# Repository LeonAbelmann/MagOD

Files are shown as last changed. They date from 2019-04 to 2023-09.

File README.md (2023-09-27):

# MagOD
Magnetic Optical Density meter
Tijmen Hageman, Jordi Hendrix, Hans Keizer, Marcel Welleweerd, Dave
van As, Ruthvik Bandaru, Rob Krawinkel, Leon Abelmann.

KIST Europe, University of Twente

## Other sources
Next to software, also the source codes to create hardware are
available here, as well as :

- Measurement head design, 3D print file (OpenSCAD, on [Thingiverse](https://www.thingiverse.com/thing:3122930) )
- Spice simulations, electronic diagrams, PCB layout (Spice, KiCad on
  [Dropbox](https://www.dropbox.com/sh/1dcai82byvd3hy0/AAA3AGXw0jbr9n2gzdcszufia))
- Laser cut pattern for housing electronics (DXF, on [Dropbox](https://www.dropbox.com/sh/1dcai82byvd3hy0/AAA3AGXw0jbr9n2gzdcszufia))

## Specifications
- Up to 800 samples per second, allows precise analysis of the rotation speed of magnetic bacteria
- Three-dimensional quasi-Helmholtz configuration, with fields up to 5 mT 
- Three color LED: red: 645 nm, 1000 mcd, green: 520 nm, 1700 mcd and blue 460 nm, 500 mcd
- Power supply with current feedback to compensate for coil heating, cut-off frequency 200 Hz
- Large area photodiode (sensitivity 0.5 mlx, with green LED theoretical max OD range of 5.8)
- Integrated pre-amplifier, SNR 83 dB (max OD range 4.0).
- Dedicated 16-bit ADS1115 DA converter
- Integrated temperature sensor
- Reference light detector
- Scattered light detector
- Fully programmable (ESP32 using Arduino IDE), open source
- User friendly spreadsheet recipe definition (csv format), with software to validate correctness
- Data collection on SD card, accessible by ftp over Wifi

## Additional info
- Marcel Welleweerd *and colleagues* (2022) ["An open-source automated magnetic optical density meter for analysis of suspensions of magnetic cells and particles"](https://doi.org/10.1063/5.0098008) Review of Scientific Instruments Vol 93, Issue 9, 094101. The manuscript can be found on [ArXiv](https://arxiv.org/abs/2106.07466)
- Chapter 8 in [Thesis](https://research.utwente.nl/en/publications/observing-magnetic-objects-in-fluids) Tijmen Hageman.
- [Presentation](https://youtu.be/TwwIsPg0qnI) by Leon Abelmann at Intermag2021

## How to join
Send mail to Leon (l.abelmann@tudelft.nl) if you are interested, all skills are welcome.

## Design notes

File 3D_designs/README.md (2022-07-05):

# Design 3D print housing
OpenScad design files and stl outputs

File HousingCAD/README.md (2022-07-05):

# CAD Design housing
Files for laser cutting housing

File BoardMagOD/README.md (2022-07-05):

# Measurement Board
Electronic design of measurement board

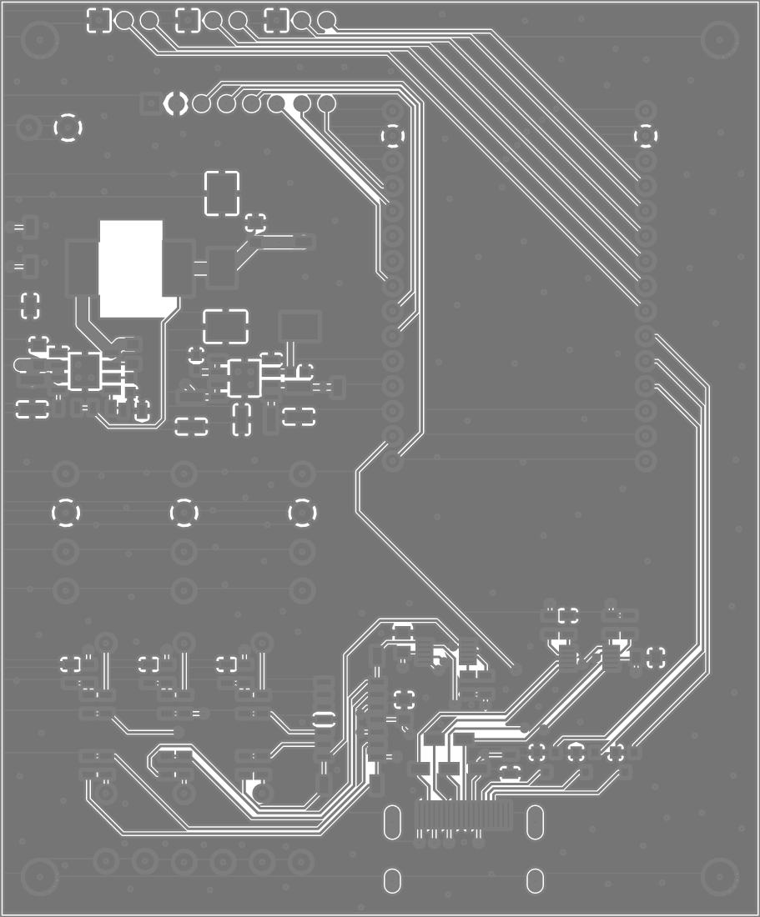
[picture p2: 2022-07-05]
BoardMagOD/mask.png

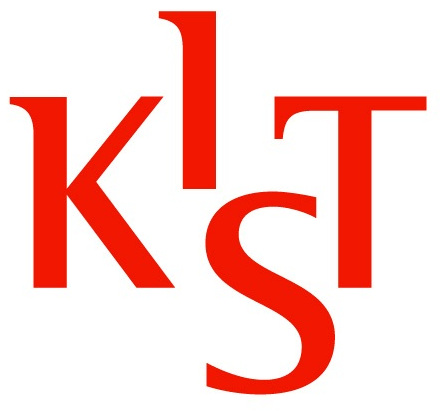
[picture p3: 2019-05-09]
matlab/MagOD_Cmag/magod.jpg

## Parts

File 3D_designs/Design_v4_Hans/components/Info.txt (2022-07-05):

Diverse components of the OD setup of Hans, Jordi and Tijmen.

Needed amount of the components:
1x coil_open
1x cuvette
1x frame
1x ledholder
1x toplid
4x coils

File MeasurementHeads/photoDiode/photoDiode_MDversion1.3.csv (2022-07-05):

Reference | Quantity | Value | Footprint | Datasheet | Article number
C1 | 1 | 0.1uF | Capacitors_SMD:C_0805 | https://nl.farnell.com/wurth-elektronik/885012207016/cap-0-1-f-10v-10-x7r-0805/dp/2534051 | 8.85012E+11
C2 C5 | 2 | C | Capacitors_SMD:C_0805 | ~
C3 | 1 | 1.5uF | Capacitors_SMD:C_0805 | https://nl.farnell.com/multicomp/mc0805x155k6r3ct/cap-1-5-f-6-3v-10-x5r-0805/dp/1759410 | MC0805X155K6R3CT
C4 | 1 | 47uF | Capacitors_SMD:C_0805 | https://nl.farnell.com/murata/grm21br60j476me15l/cap-47-f-6-3v-20-x5r-0805/dp/2362109 | GRM21BR60J476ME15L
D1 | 1 | BPW21 | Package_TO_SOT_THT:TO-5-2_Window | http://techwww.in.tu-clausthal.de/site/Dokumentation/Dioden/Fotodioden/BPW21-Fotodiode.pdf | BPW21R
D2 | 1 | D | Diodes_SMD:D_SOD-123 | ~
J1 | 1 | Conn_01x03 | Connector_Molex:Molex_Pico-Clasp_501331-0307_1x03-1MP_P1.00mm_Vertical | https://nl.farnell.com/molex/501331-0307/connector-header-3pos-1row-1mm/dp/1835977?st=pico%20clasp | 501331-0307
L1 | 1 | Ferrite_Bead | Inductor_SMD:L_0805_2012Metric | https://nl.farnell.com/murata/blm21bd272sn1l/ferrite-bead-0-8ohm-200ma-0805/dp/1515647 | BLM21BD272SN1L
MH1 MH2 | 2 | MountingHole | Mounting_Holes:MountingHole_2.2mm_M2 | ~
R1 R3 R4 R6 | 4 | R | Resistor_SMD:R_0805_2012Metric | ~
R2 | 1 | 3 | Resistor_SMD:R_0805_2012Metric | https://nl.farnell.com/panasonic-electronic-components/erj6geyj3r0v/res-3r-5-0-125w-0805-thick-film/dp/2323844RL | ERJ6GEYJ3R0V
U1 | 1 | Opamp_Dual_Generic | Housings_SOIC:SOIC-8_3.9x4.9mm_Pitch1.27mm | https://nl.mouser.com/ProductDetail/Texas-Instruments/OPA2140AID | OPA2140AID
U2 | 1 | EMIshield | EMIshield:Laird-BMI-S-202-F | https://nl.farnell.com/laird/bmi-s-202-f/emi-shield-surface-mount/dp/2497717?ost=BMI-S-202-F&scope=partnumberlookahead&searchref=searchlookahead | BMI-S-202-F

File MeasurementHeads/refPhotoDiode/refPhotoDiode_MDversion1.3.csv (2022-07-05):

Id | Designator | Package | Quantity | Designation | Supplier and ref
1 | R1,R2 | R_0805_2012Metric | 2 | R
2 | C1,C4 | C_0805 | 2 | C
3 | C2 | C_0805 | 1 | 1.5uF
4 | C3 | C_0805 | 1 | 0.1uF
5 | L1 | L_0805_2012Metric | 1 | Ferrite_Bead
6 | J1,J2 | PinHeader_1x04_P2.54mm_Vertical_SMD_Pin1Left | 2 | Conn_01x04
7 | U2 | Wurth-3610213126S-EMIshield-13.26x12.3mm | 1 | EMIshield
8 | REF** | MountingHole_2.2mm_M2 | 1 | MountingHole_2.2mm_M2
9 | J3 | Molex_Pico-Clasp_501331-0607_1x06-1MP_P1.00mm_Vertical | 1 | Conn_01x06
10 | D2 | D_SOD-123 | 1 | D
11 | D1 | TO-5-2_Window | 1 | BPW21
12 | U1 | SOT-23-5 | 1 | OPA140

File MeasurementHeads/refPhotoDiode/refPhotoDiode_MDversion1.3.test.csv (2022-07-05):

Reference |  | Value |  | Footprint | Datasheet | Article | number
D1 | BPW21 | BPW21:TO-5-2_Window | http://techwww.in.tu-clausthal.de/site/Dokumentation/Dioden/Fotodioden/BPW21-Fotodiode.pdf
C1 | 180p | Capacitors_SMD:C_0805 | ~
R1 | 1000k | Resistor_SMD:R_0805_2012Metric | ~
J1 | Conn_01x04 | Connector_PinHeader_2.54mm:PinHeader_1x04_P2.54mm_Vertical_SMD_Pin1Left | https://nl.farnell.com/samtec/tsm-104-04-t-sv/header-2-54mm-smt-4way/dp/2043897 | TSM-104-04-T-SV
J2 | Conn_01x04 | Connector_PinHeader_2.54mm:PinHeader_1x04_P2.54mm_Vertical_SMD_Pin1Left | https://nl.farnell.com/samtec/tsm-104-04-t-sv/header-2-54mm-smt-4way/dp/2043897 | TSM-104-04-T-SV
J3 | Conn_01x06 | Connector_Molex:Molex_Pico-Clasp_501331-0607_1x06-1MP_P1.00mm_Vertical | https://nl.farnell.com/molex/501568-0607/header-1-00mm-6way/dp/2060673?st=molex%20pico | 501331-0607
C2 | 1.5uF | Capacitors_SMD:C_0805 | https://nl.farnell.com/multicomp/mc0805x155k6r3ct/cap-1-5-f-6-3v-10-x5r-0805/dp/1759410 | MC0805X155K6R3CT
U2 | EMIshield | EMIshield:Wurth-3610213126S-EMIshield-13.26x12.3mm | https://nl.farnell.com/wurth-elektronik/3610213126s/emi-shield-cabinet-13-26mm-x-12/dp/2918354?ost=3610213126S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 | 3610213126S
L1 | Ferrite_Bead | Inductor_SMD:L_0805_2012Metric | https://nl.farnell.com/murata/blm21bd272sn1l/ferrite-bead-0-8ohm-200ma-0805/dp/1515647 | BLM21BD272SN1L
C3 | 0.1uF | Capacitors_SMD:C_0805 | https://nl.farnell.com/wurth-elektronik/885012207016/cap-0-1-f-10v-10-x7r-0805/dp/2534051 | 885012207016
R2 | 20k | Resistor_SMD:R_0805_2012Metric | ~
D2 | D | Diodes_SMD:D_SOD-123 | ~
C4 | 1u | Capacitors_SMD:C_0805 | ~
U1 | OPA140 | Package_TO_SOT_SMD:SOT-23-5 | http://www.ti.com/lit/ds/symlink/opa340.pdf

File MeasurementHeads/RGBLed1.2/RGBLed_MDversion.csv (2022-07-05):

Reference | Quantity | Value | Footprint | Datasheet
D1 | 1 | LED_RABG | KingbrightRGB:L-154A4SUREQBFZGEW | ~
J1 J2 | 2 | Conn_01x04 | Socket_Strips:Socket_Strip_Straight_1x04_Pitch2.54mm | ~
R1 R2 R3 | 3 | R | Resistors_SMD:R_0805 | ~

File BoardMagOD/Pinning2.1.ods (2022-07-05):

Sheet: SPI
ESP32 |  |  | ESP32 DEVKIT V1 J2 |  |  | MagBoard U3 |  |  | MagODBoard J3 |  |  | J3 flatcable | TFTM050Board |  |  | ES-AR-RA8875 | ES-AR-RA8875 | 74lv245 | Arduino |  | ES-AR-RA8875
 |  |  |  |  |  |  |  |  | 1 | 5V_b | red | brown | 3-4 | VDD | 1-8 JP1 | LCD-VDD | JP4-4 |  | Arduino 5V | JP4-4 | JP1-3/4
 |  |  |  |  |  |  |  |  | 2 | GND | black | red | 1-2 | VSS |  | VSS | JP4-3 |  | GND | Jp4-3 | JP1-1/2
37 | GPIO23 | low | VSPI_MOSI | 15 | GPIO23 | 30 | D23 | MOSI | 3 | MOSI_con | green | orange | 7 | SDI (MOSI) |  | CS-SDI-SDA | JP5-3 | U2 B2-A2 | MOSI | JP5-3 | JP1-7
31 | GPIO19/CTS0 | high | VSPI_MISO | 10 | GPIO19 | 25 | D19 | MISO | 4 | MISO_con | purple | yellow | 6 | SDO (MISO) |  | WR/SDO | JP5-6 | U1 A0-B0 | MISO | JP5-6 | JP1-6
30 | GPIO18 | low | VSPI_SCK | 9 | GPIO18 | 24 | D18 | SCK | 5 | SCK_con | white | green | 8 | SCLK |  | RS/SCLK | JP5-4 | U1 B2-A2 | SCLK | JP5-4 | JP1-8
29 | GPIO5 | high | VSPI_SS | 8 | GPIO5 | 23 | D5 | CS | 6 | CS | grey | blue | 5 | CS |  | RD/CS | JP8-3 | U1 B1-A1 | IO10 | JP8-3 | JP1-5
28 | TX2 | high | TX2 | 7 | GPIO17 | 22 | TX2 | RST | 7 | RST_Con | yellow | purple | 11 | RESET | 9-14 JP3 | RESET | JP8-2 | U1 B4-A4 | IO9 | JP8-2 | JP1-11
27 | RX2 | high | RX2 | 6 | GPIO16 | 21 | RX2 | INT | 8 | INT | brown | gray | 10 | INT OUT
 |  |  |  |  |  |  |  |  |  |  |  |  | 9 | WAIT
 |  |  |  |  |  |  |  |  |  |  |  |  | 12 | MCU Int.select
 |  |  |  |  |  |  |  |  |  |  |  |  | 13 | GND
 |  |  |  |  |  |  |  |  |  |  |  |  | 14 | BL-Control
 |  |  |  |  |  |  |  |  | MagODBoard J24
23 | GPIO15/AD2_3/T3/SD_CMD |  | HSPI_CS | 6 | GPIO15 | 18 | D15 |  | 2 | CS2
 |  |  |  |  |  | See above |  |  | 3 | MOSI
 |  |  |  |  |  | See above |  |  | 5 | SCK
 |  |  |  |  |  | See above |  |  | 7 | MISO
 |  |  |  |  |  |  |  |  | 4 | VCC
 |  |  |  |  |  |  |  |  | 6 | GND

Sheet: MotorDrivers
 | MagOD |  |  | MD13S | Coils
 | J2-1 | GND | black | GND (1)
U3-D33 | J2-2 | PMW_X | white | PWM (3)
U3-D25 | J2-3 | DIR_X | yellow | DIR (4)
 | J4-1 | GND | black | GND (1)
U3-D26 | J4-2 | PMW_Y | white | PWM (3)
U3-D27 | J4-3 | DIR_Y | yellow | DIR (4)
 | J6-1 | GND | black | GND (1)
U3-D14 | J6-2 | PMW_Z | white | PWM (3)
U3-D12 | J6-3 | DIR_Z | yellow | DIR (4)
 | J14-2 | I1_A | blue | MA-x
 | J14-1 | I1-B | yellow | MB-x
 | J14-3 | GND | black | “-”
 | J14-4 | 12V | red | “+”
 | J18-2 | I1_A | blue | MA-y
 | J18-1 | I1-B | yellow | MB-y
 | J18-3 | GND | black | “-”
 | J18-4 | 12V | red | “+”
 | J19-2 | I1_A | blue | MA-z
 | J19-1 | I1-B | yellow | MB-z
 | J19-3 | GND | black | “-”
 | J19-4 | 12V | red | “+”
 | J9-6 | I_sense1 |  |  | Coil_X+
 | J9-5 | I1_B |  |  | Coil_X-
 | J9-4 | I_sense2 |  |  | Coil_Y+
 | J9-3 | I2_B |  |  | Coil_Y-
 | J9-2 | I_sense3 |  |  | Coil_Z+
 | J9-1 | I3_B |  |  | Coil_Z-

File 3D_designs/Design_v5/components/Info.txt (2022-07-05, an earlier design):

Components:
4x coil
1x cuvette_tube
1x frame
1x led_holder
1x top_coil
2x top_lid

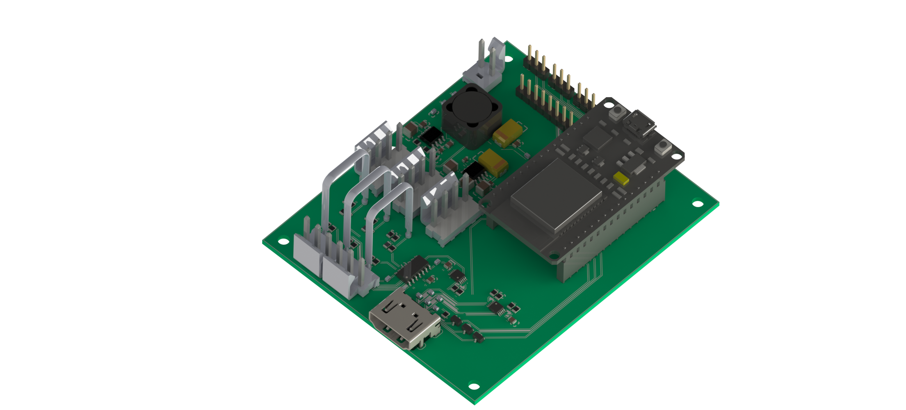
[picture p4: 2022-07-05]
BoardMagOD/ComponentsView.png

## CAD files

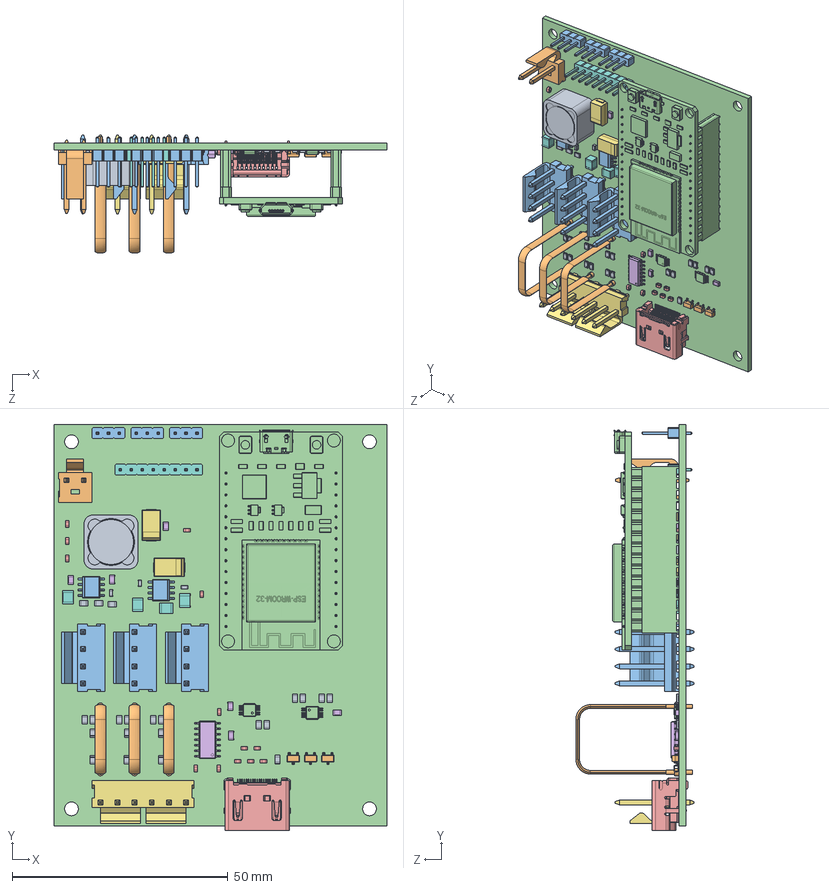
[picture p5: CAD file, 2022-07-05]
BoardMagOD/ODMeter2.1.SLDASM
77.0 x 94.0 x 27.4 mm
COMPOUND.step
SOLID.step
COMPOUND-0.step x 2
COMPOUND-1.step
COMPOUND-2.step
SOLID-3.step x 6
SOLID-4.step
SOLID-5.step
SOLID-6.step x 28
SOLID-7.step x 3
SOLID-8.step x 3
SOLID-9.step x 2
SOLID-10.step x 13
SOLID-11.step
SOLID-12.step x 2
SOLID-13.step x 4
SOLID-14.step x 3
SOLID-15.step x 3
SOLID-16.step x 3
COMPOUND-17.step

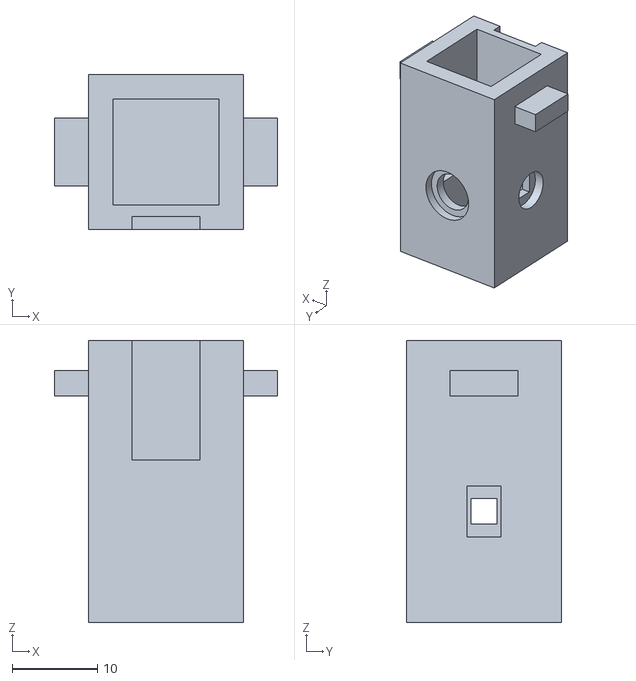
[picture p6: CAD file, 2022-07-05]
3D_designs/Design_v4_Hans/components/stl_files/design_v4_Hans_cuvette.stl
26.1 x 18.1 x 33.0

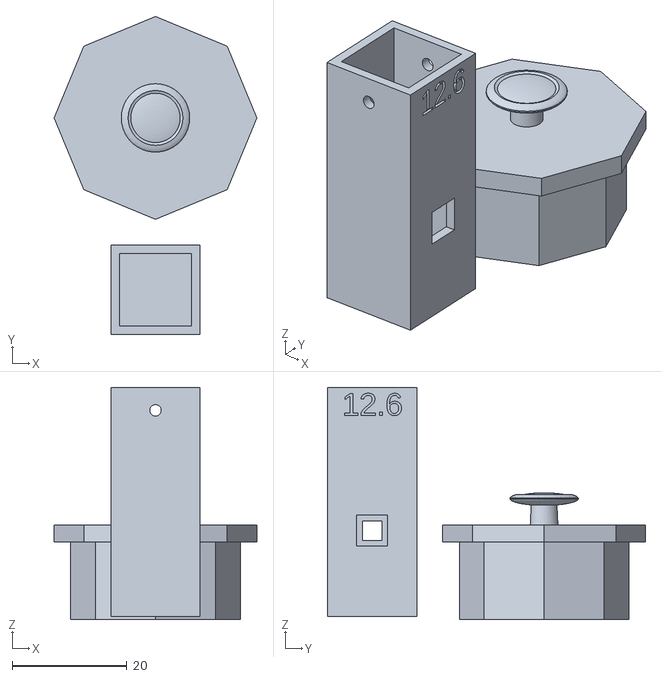
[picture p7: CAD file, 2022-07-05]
3D_designs/Design_v7/MagOD_v7.stl
35.4 x 55.5 x 40.5

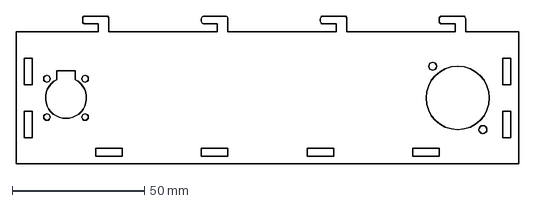
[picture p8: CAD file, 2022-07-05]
HousingCAD/CoilHousing/long_side2.dxf
190.0 x 56.0 mm

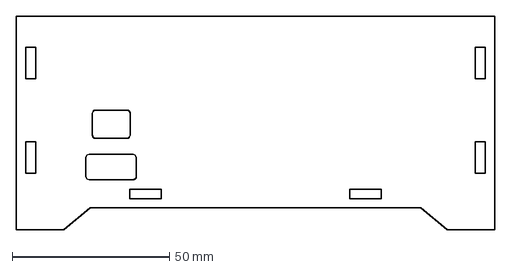
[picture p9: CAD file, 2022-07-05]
HousingCAD/InstrumentHousing/achterkant2.dxf
152.0 x 68.0 mm

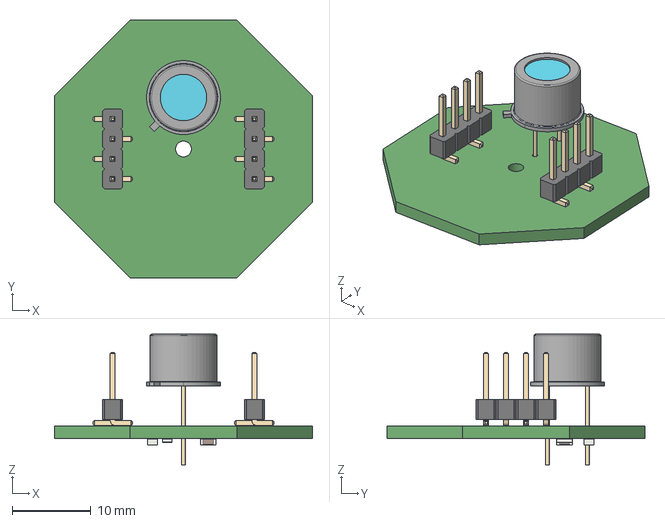
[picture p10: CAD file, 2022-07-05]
MeasurementHeads/refPhotoDiode/refPhotoDiode_MDversion1.3.step
32.8 x 32.8 x 16.6 mm

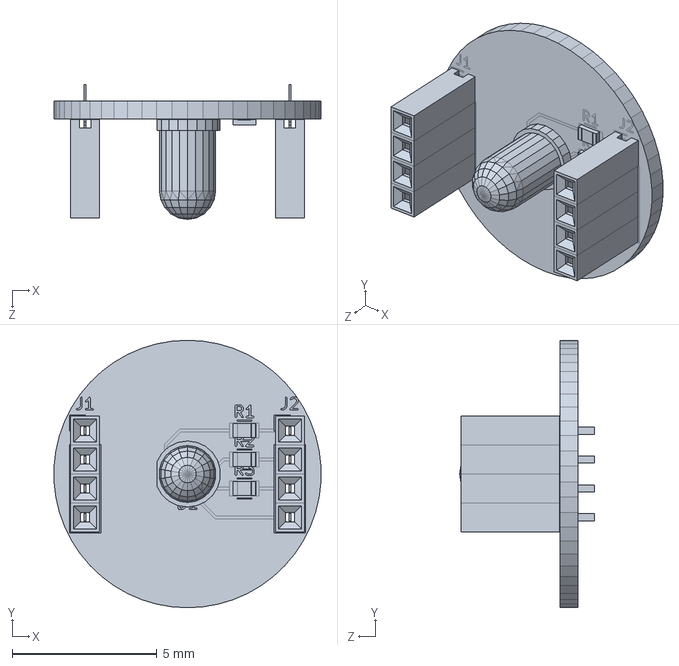
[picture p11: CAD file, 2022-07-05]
MeasurementHeads/RGBLed1.2/rgbled_mdversion.wrl.sldprt
9.24 x 9.25 x 4.66 mm

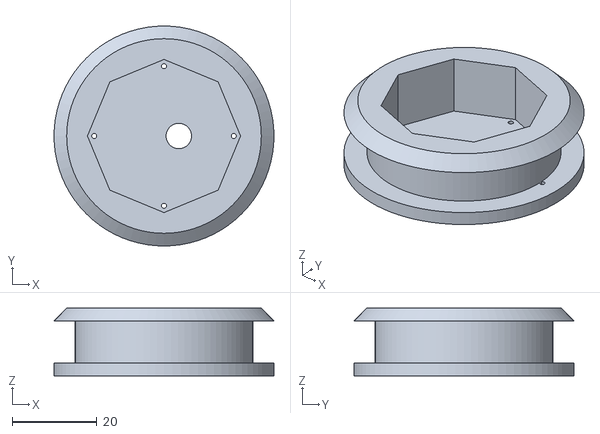
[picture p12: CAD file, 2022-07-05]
3D_designs/Design_v4_Hans/components/stl_files/design_v4_Hans_coils.stl
52.0 x 52.0 x 16.0

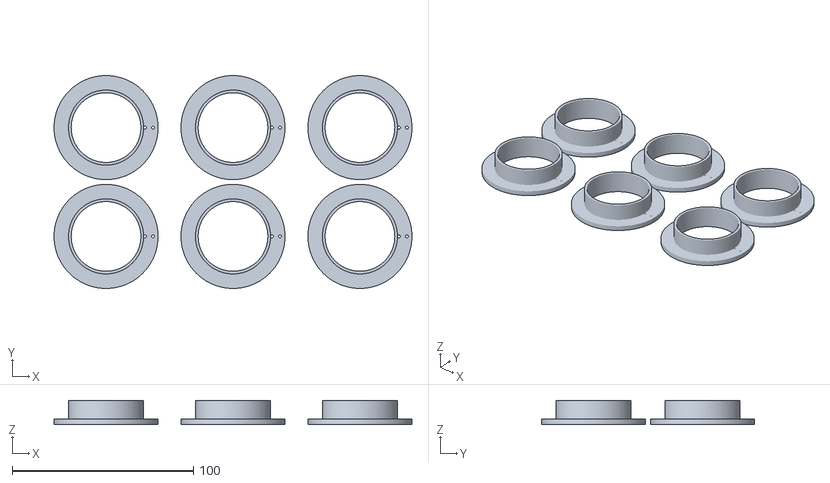
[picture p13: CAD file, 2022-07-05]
3D_designs/Design_v7/MagOD_v7_coil_covers.stl
197.4 x 117.4 x 13.2

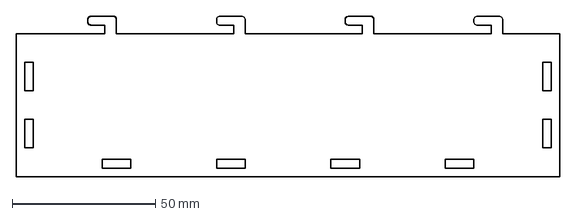
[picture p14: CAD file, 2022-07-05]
HousingCAD/CoilHousing/long_side1.dxf
190.0 x 56.0 mm

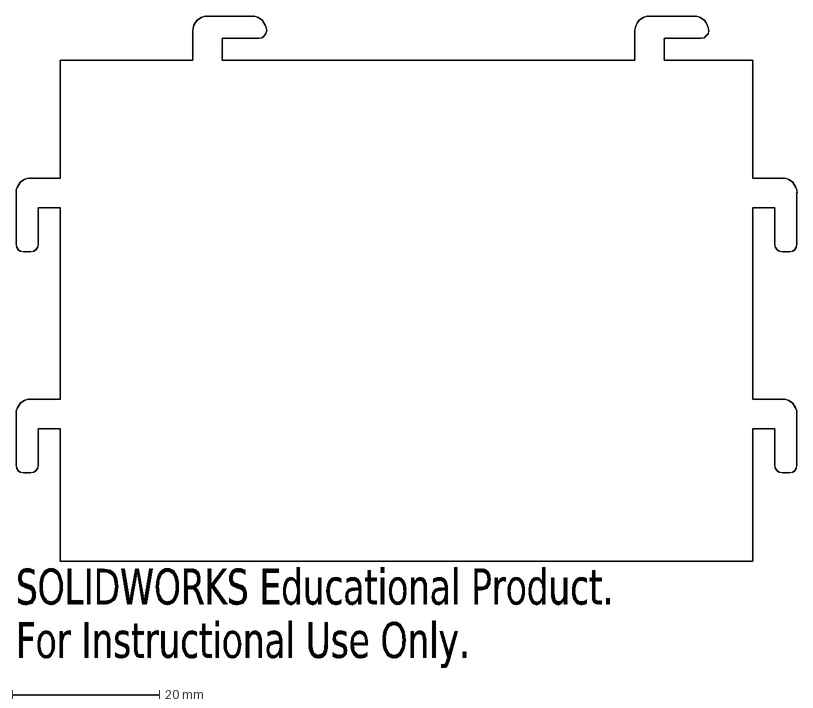
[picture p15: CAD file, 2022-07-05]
HousingCAD/InstrumentHousing/zijkant_s (2x).dxf
SOLIDWORKS Educational Product.
For Instructional Use Only.

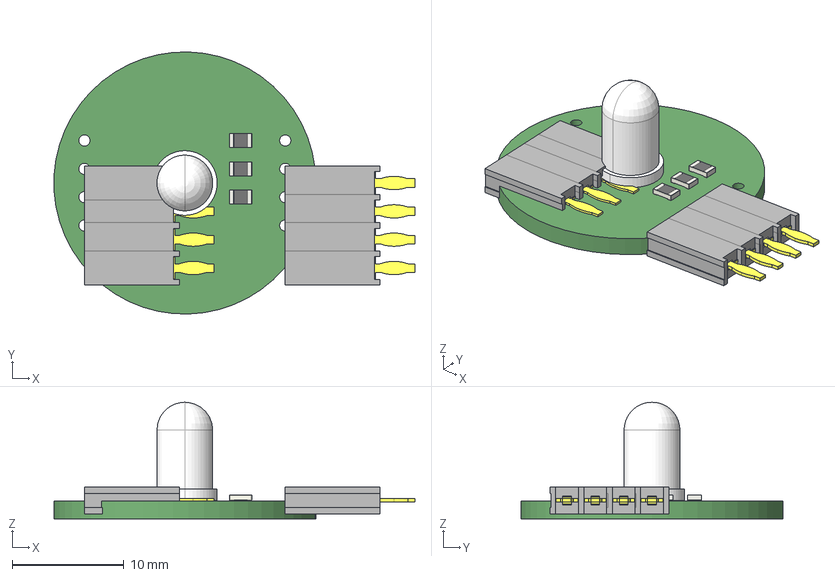
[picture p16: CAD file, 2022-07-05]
MeasurementHeads/RGBLed1.2/RGBLed_MDversion.step
32.4 x 23.5 x 10.5 mm

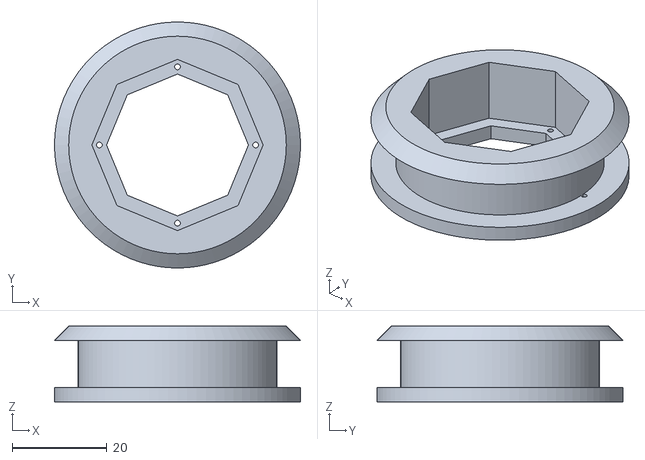
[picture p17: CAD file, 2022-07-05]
3D_designs/Design_v4_Hans/components/stl_files/design_v4_Hans_coil_open.stl
52.0 x 52.0 x 16.0

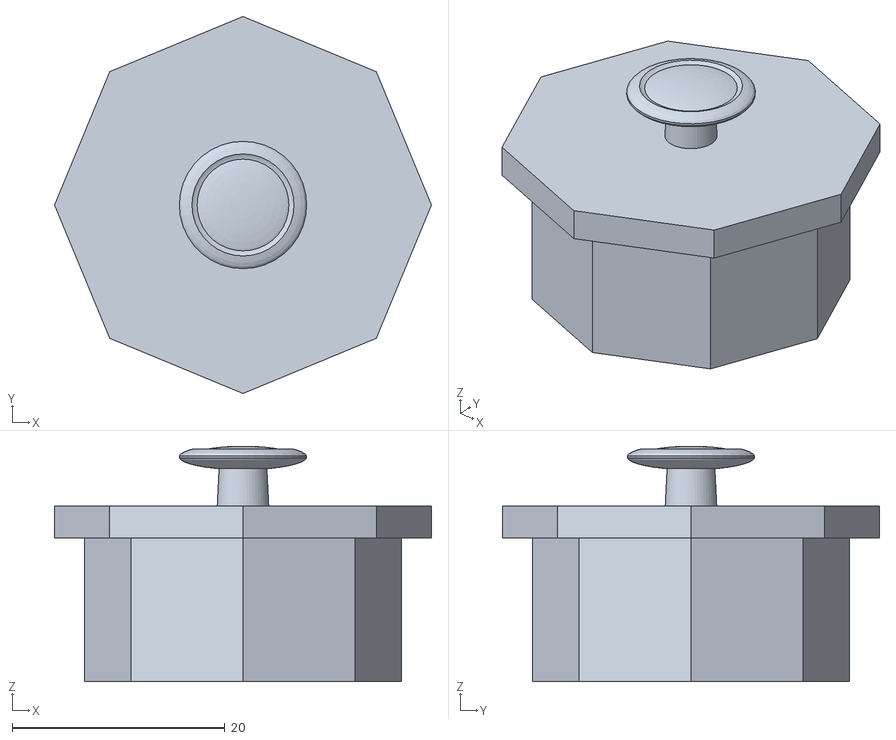
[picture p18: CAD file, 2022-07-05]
3D_designs/Design_v7/MagOD_v7_cap.stl
35.4 x 35.4 x 22.1

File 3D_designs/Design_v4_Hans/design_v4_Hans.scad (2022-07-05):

$vpd=100;
$fn=80;

T = 3; //wall thickness in mm
depth_coil=5;

coil_w = 10;
coil_h = 5;
coil_r = 21;
coil_r1 = 22+9-depth_coil;
coil_r2 = 8;
hole_r = 0;
coil_spacing = 23.1;
//coil_spacing = 72;

play = 0.2;
play_cuvette = 0.3;

Wcuv = 12.1; //cuvette width
Hcuv = 30; //cuvette holder height

//translate([-50,0,0]) rotate([180,0,0]) rotate([0,-90,0]) coil_holder();
//translate([0,80,0]) rotate([0,90,-90]) cam_tube_holder();

    translate([80,0,0])
    union(){
    
        rotate([0,-90,0])   translate([0,0,coil_spacing+0.5*coil_r-2*T])  coil_spindle(coil_w, coil_h, coil_r, coil_r-2*T); //LED coil
                //add LED holder
            LEDtube_L = 30;
            translate([LEDtube_L/2+frame_len/2-T,0,0]) rotate([0,90,0])
            union(){
                //create extension tube        
                cylinder_hollow(LEDtube_L, coil_r-2*T, coil_r-3*T, true);
                LED_d = 5;
                difference(){
                    //lid of extension tube
                    translate([0, 0, LEDtube_L/2-T/2]) cylinder(h=T, r1=coil_r-2*T, r2=coil_r-2*T, center=true);
                    //hole for LED
                    translate([0, 0, LEDtube_L/2-T/2]) cylinder(h=T, d1=LED_d, d2=LED_d, center=true);
                }
            }
            
        }



difference(){
    union(){
        
        translate([0,0,-10-T]) cuvette_tube();        
        
        //coil sets
        rotate([0,0,0])     translate([0,0,-coil_spacing])  coil_spindle(coil_w, coil_h, coil_r, hole_r); //bottom coil
        rotate([0,180,0])   translate([0,0,-coil_spacing])  coil_spindle(coil_w, coil_h, coil_r, coil_r-2*T); //top coil (with lid hole)
        rotate([0,90,0])    translate([0,0,-coil_spacing])  coil_spindle(coil_w, coil_h, coil_r, hole_r);  //PD coil
        
        rotate([90,90,0])    translate([0,0,-coil_spacing])  coil_spindle(coil_w, coil_h, coil_r, hole_r);  //camera coil

        rotate([-90,-90,0]) translate([0,0,-coil_spacing])  coil_spindle(coil_w, coil_h, coil_r, hole_r); //non-camera coil
        
        //top lid
        translate([0,0,50]) top_lid();
        
        translate([0,0,-37.7]) rotate([0,180,0]) 
        bottom_lid();

        //coil frame (cuvette holder excluded)
        frame_len = 72;
        difference(){
            coil_frame(frame_len);
            //cut out cuvette
            translate([0,0,-10-T]) cuvette_cube();
            //holes
            holeD = 0.9;
            hole_spacing = 23.1;
            rotate([0,0,0])     translate([0,0,-hole_spacing])  coil_holes(coil_w, coil_h, coil_r, hole_r, holeD); //bottom coil
            rotate([0,180,0])   translate([0,0,-hole_spacing])  coil_holes(coil_w, coil_h, coil_r, coil_r-2*T, holeD); //top coil (with lid hole)
            rotate([0,90,0])    translate([0,0,-hole_spacing])  coil_holes(coil_w, coil_h, coil_r, hole_r, holeD);  //PD coil
            rotate([0,-90,0])   translate([0,0,-hole_spacing])  coil_holes(coil_w, coil_h, coil_r, coil_r-2*T, holeD); //LED coil
            rotate([90,90,0])   translate([0,0,-hole_spacing])  coil_holes(coil_w, coil_h, coil_r, coil_r-2*T, holeD); //camera coil
            rotate([-90,-90,0]) translate([0,0,-hole_spacing])  coil_holes(coil_w, coil_h, coil_r, hole_r, holeD); //non-camera coil
        }          
    }
//    
    //camera hole
    translate([0, 20, 0]) cube([1.3*Wcuv, 20, 1.6*Wcuv], center=true);
    
    //camera hole other side
    translate([0, -20, 0]) cube([1.3*Wcuv, 20, 1.6*Wcuv], center=true);

//    
    //open up structure
    //rotate([0,0,90]) translate([0,25,0]) cube([140,50,120],center=true);
}

module top_lid(){
    
    union(){
        translate([0,0,0]) hex_hollow(8, T, coil_r-T, 0);
        translate([0,0,-1.5*T]) hex_hollow(8, 2*T, coil_r-2*T-play/2, coil_r-3*T-play/2);
    }
    
}

module coil_holder(){
   difference(){
        //cylinder(h=T, r1=coil_r-T, r2=coil_r-T, center=true);
        polyN(8, T*2, coil_r-T);
        holeD = 0.9;
        translate([0,0,10]) coil_holes(coil_w, coil_h, coil_r, hole_r, holeD);
    }
    polyN = 7;
    polyH = 30;
    polyR = 3;
    translate([0,0,polyH/2+T/2]) polyNflat(polyN, polyH, polyR);
}
module coil_frame(frame_len){
    
    difference(){
        union(){
            //basic structure
            difference(){
                //outer structure
                union(){
                    rotate([0,0,0])     polyN(8, frame_len, coil_r-T);
                    rotate([0,90,0])    polyN(8, frame_len, coil_r-T);
                    rotate([90,0,0])    polyN(8, frame_len, coil_r-T);
                }
                //free inner structure
                union(){
                        rotate([0,0,0])     polyN(8, frame_len, coil_r-2*T); 
                        rotate([0,90,0])    polyN(8, frame_len, coil_r-2*T); 
                        rotate([90,0,0])    polyN(8, frame_len, coil_r-2*T); 
                }
                
            }  
            
            //create support for cuvette holder
            difference(){
                rotate([0,90,0]) polyN(8, frame_len, coil_r-T);
                rotate([0,90,0]) polyN(8, frame_len, coil_r-2*T);
                translate([0,0,15]) cube(Wcuv, center=true);
            }
            translate([7,0,0]) rotate([0,90,0]) polyN(8,T,coil_r-2*T);
            

        }
        
        //drill cable holes
        hole_d = 3;
        hole_h = T+2;
        translate([-20,0,-coil_r+1.5*T]) cylinder(h=hole_h, d1=hole_d, d2=hole_d, center=true);
        translate([20,0,-coil_r+1.5*T]) cylinder(h=hole_h, d1=hole_d, d2=hole_d, center=true);  
    }
    
}



module coil_spindle(coil_w, coil_h, coil_r, hole_r){   
   
    translate([0,0,-coil_w/2-T])
    union(){
        
        //major cylinder
        cylinder_hollow_hex(coil_w+2*T, coil_r, coil_r-T+play/2, true);
        
        //tapered edge on one side
        intersection(){
            translate([0,0,coil_w/2+T/2]) cylinder_hollow(T, coil_r+coil_h, coil_r-T+play, true);
            translate([0,0,coil_w/2+T/2]) cylinder(h=T, r1=coil_r+coil_h, r2 = coil_r+coil_h-T, center=true);
        }
        
        
        //holed edge on other side
        difference(){
            translate([0,0,-coil_w/2-T/2]) cylinder_hollow_hex(T, coil_r+coil_h, hole_r, true);

            coil_holes(coil_w, coil_h, coil_r, hole_r, 1.2);
    
        }
        
    }   
    
    
}    
    


module coil_holes(coil_w, coil_h, coil_r, hole_r, holeD){
  
    //screw holes
    hole_screwD = holeD;
    screwLen = 8;
    Nscrew = 4;
    thetaStep = 360/Nscrew;
    for(i=[0:Nscrew-1]){
        r = coil_r-1.5*T;
        rotate([0,0,i*thetaStep]) translate([r,0,-coil_w-T+screwLen/2]) cylinder(h=screwLen, d1=hole_screwD, d2=hole_screwD, center=true);
    }
    
    //screw holes for coil
    hole_screwD1 = holeD;
    screwLen1 = 8;
    Nscrew1 = 1;
    thetaStep1 = 360/Nscrew1;
    for(i=[0:Nscrew1-1]){
        r = coil_r1-1.5*T;
        rotate([0,0,i*thetaStep1]) translate([r,0,-coil_w-T+screwLen/2]) cylinder(h=screwLen1, d1=hole_screwD1, d2=hole_screwD1, center=true);
    }
    
        //screw holes for wiring
    hole_screwD2 = 6;
    screwLen2 = 8;
    Nscrew2 = 1;
    thetaStep2 = 360/Nscrew2;
    for(i=[0:Nscrew2-1]){
        r = coil_r2-1.5*T;
        rotate([0,0,i*thetaStep2]) translate([r,0,-coil_w-T+screwLen2/2]) cylinder(h=screwLen2, d1=hole_screwD2, d2=hole_screwD2, center=true);
    }

}

module cylinder_hollow(height, radius_outer, radius_inner, cent){
    difference(){
        cylinder(h=height, r1=radius_outer, r2=radius_outer, center=cent);
        cylinder(h=height, r1=radius_inner, r2=radius_inner, center=cent);
    }
}

module cylinder_hollow_hex(height, radius_outer, radius_inner, cent){
    difference(){
        cylinder(h=height, r1=radius_outer, r2=radius_outer, center=cent);
        polyN(8, height, radius_inner);
    }
}
module hex_hollow(N, height, radius_outer, radius_inner){
    difference(){
        polyN(N, height, radius_outer);
        polyN(N, height, radius_inner);
    }
}

module cuvette_tube (  ) {

    difference(){

        //Basic tube
        translate([-Wcuv/2-T, -Wcuv/2-T, 0])
        difference(){
            cube([Wcuv+2*T, Wcuv+2*T, Hcuv+T], center=false);
            translate([T-play_cuvette/2, T-play_cuvette/2, T]) cube([Wcuv+play_cuvette, Wcuv+play_cuvette, Hcuv+1], center=false);
        }
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

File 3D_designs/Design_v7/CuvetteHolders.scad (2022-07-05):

/* Magnetic OD meter
   Version 1: Feb 2020, Leon Abelmann
   Individual cuvette holder to accomdate different types of cuvettes. You can vary the cuvette width using Wcuv. This version has the cuvette with written on the holder. You can also vary the depth of the cuvette, in order to change the distance of the bottom of the cuvette to the light beam, for marathon tests (with MC-1 e.g.). This version has a small holes as well, so that it is more easy to remove the cuvetteholder from the frame.
   Width 12.6 goes very well with the plastic cuvettes we have in the lab (Brand 959150)
*/

 
//$vpd=400; //Viewport, defines the zoom factor after auto reload
$fn=80; //High res
//$fn = 20; //Low res for testing

//General
T = 3; //wall thickness in mm
play = 0.2; // Space between the parts (so that they don't jam)

//Cuvette
Wcuv = 12.4;       //cuvette width (now parameter)
Hcuv = 40;           //cuvette holder height
WcuvOut = Wcuv+T;    //cuvette holder outer width
slit_H = 10;         //height of slits (w.r.t. cuvette)
slit1_H = 5;         //LED slit height
slit1_W = 5;         //LED slit width
slit2_H = 3;         //Photodiode slit height
slit2_W = 3;         //Photodiode slit width
slit2_dist = 3;      //secondary slit spacing
slit3_W = 4;         //Scatter diode slit width
slit3_H = 4;         //Scatter diode slit height
radius_photo = 4.1;  //radius of photodiode
radius_photo2 = 3;   //radius of photodiode
radius_photo3 = 4.2; //radius of photodiode
width_connector = 3; //width of Molex 4p connector
height_connector = 5;//height of Molex 4p connector
slit_diff=slit2_H-slit1_H; //Help

//Coils
depth_coil=5;
coil_w = 10;
coil_h = 5;
coil_r = 21;
coil_r1 = 22+9-depth_coil;
coil_r2 = 8;
hole_r = 0;
coil_spacing = 23.1;
//coil_spacing = 72;

// Individual components in one field
translate([0,0,slit_H+T+slit1_H/2])
cuvette_insert(12.5,10); // (Inner width, height center slit to bottom) 

translate([0,20,slit_H+T+slit1_H/2])
cuvette_insert(12.6,10); // (Inner width, height center slit to bottom)

translate([0,40,slit_H+T+slit1_H/2])
cuvette_insert(12.7,10); // (Inner width, height center slit to bottom)

translate([0,60,slit_H+T+slit1_H/2])
cuvette_insert(12.7,4); // (Inner width, height center slit to bottom)


/* Designed to have different inserts for differen cuvette sizes Wcuv and
 different distances between bottom insert and photodiode slits slit_H*/
// Wcuv: space left for the cuvette. The Hellma are 12.4 mm.
// Slit_H
module cuvette_insert(Wcuv,slit_H) {
     radius=coil_r-T;
     difference()
     {
	  translate([-WcuvOut/2, -WcuvOut/2, -radius+T])
	  {/*Hollow cube with inner ridge Wcuv and with bottom */
	       /* such that distance to center of slits is slit_H */
	       difference(){
		    cube([WcuvOut, WcuvOut, Hcuv], center=false);

		    /* hollow inside */
		    translate([(WcuvOut-Wcuv)/2,
			       (WcuvOut-Wcuv)/2,
			       radius-T-slit_H])
			 cube([Wcuv, Wcuv, Hcuv+2],
			      center=false);

		    /* text on side */
		    translate([WcuvOut-0.49,WcuvOut/2,Hcuv-3])
			 rotate([90,0,90])
			 textemboss(str(Wcuv));
		    translate([0.49,WcuvOut/2,Hcuv-3])
			 rotate([90,0,-90])
			 textemboss(str(slit_H));

		    /* small holes for easy removal */
		    translate([Wcuv/2+T/2,0,Hcuv-4])
			 rotate([90,0,0])
			 cylinder(h=2*T,r1=1,r2=1,center=true);
		    translate([Wcuv/2+T/2,Wcuv,Hcuv-4])
			 rotate([90,0,0])
			 cylinder(h=2*T,r1=1,r2=1,center=true);
	       }		    
	  }
	  union(){
	       // LED slit (entry for light)
	       translate([Wcuv/2, 0 ,0])
		    cube([2*T+1, slit1_W+play,
			  slit1_H+play], center=true);
	       //Photodiode slit
	       translate([-Wcuv/2-T/2,0, slit1_H/2+slit_diff/2])
		    translate([1, 0, -slit2_dist/2])
		    cube([T+1, slit2_W+play, slit2_H+play], center=true);
	       //Scatter diode slit
	       translate([0, (Wcuv/2+1.5*T)-1 ,0])
		    rotate([90,90,0])
		    cylinder(h=3*T, r1=radius_photo2+play,
			     r2=radius_photo2+play, center=true);
	  }
     }
}

module textemboss(string) {
     linear_extrude(height = 0.5) {
	  text(string, size = 4, halign = "center", valign = "center", $fn = 16);}
}

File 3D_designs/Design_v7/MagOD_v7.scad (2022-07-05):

/* Magnetic OD meter
 Version 7.2: Nov 2020, Leon Abelmann
 Enlarged openings for pico adapters
 Extruded bottom part so that wires can be guided out
 Enlarged slit for NTC
 
 Version 7.1: July 2020, Leon Abelmann
 Differences: Reduced coil diameter a little, so that the coils fit better. Also got rid of guessed length for frame, now it is nicely calculated.

Version 7:
- Adapted coil holder for Janzten Audio 000-0996 2.9 mH 2.1 Ohm coils

 Version 6:
 - Double cuvette holder. Now you can take out inner cuvette without having to move the photodiode
 
Version 5: May 2018, Leon Abelmann
 Differences with version 4 of Hans Keizer
 - Made top lid longer, to accomodate cuvettes with plug
 - Made the insert 0.3 mm bigger to 12.3, so that cuvettes slide in more easily
*/
 
$vpd=300; //Viewport, defines the zoom factor after auto reload
$fn=80; //High res
//$fn = 20; //Low res for testing

//General
T = 3; //wall thickness in mm
play = 0.4; // Space between the parts (so that they don't jam)

//Coils
coil_w = 20.5;//Width of the coil, so space available for the windings
coil_h = 6;   // Height of the coil windings
coil_r = 20.7;  // Inner diameter of coils
hole_r = 0.8; //Radius of holes for wiring

//Frame
frame_len = 2*(coil_w+coil_r+2*T-play);//Length of the frame
hex_r = 21; /* Radius of the hexagons that hold the coils. Should be smaller than the coil inner radius coil_r! */

//Cuvette
Wcuv = 12.6;         //cuvette width (can vary from cuvette to cuvette!)
play_cuvette = 0.3;  //how much room do you want around the cuvette
Hcuv = 40;           //cuvette holder height
WcuvOut = Wcuv+T;    //cuvette holder outer width
slit_H = 10;         //height of slits (w.r.t. cuvette)
slit1_H = 5;         //LED slit height
slit1_W = 5;         //LED slit width
slit2_H = 3;         //Photodiode slit height
slit2_W = 3;         //Photodiode slit width
slit2_dist = 3;      //secondary slit spacing
slit3_W = 4;         //Scatter diode slit width
slit3_H = 4;         //Scatter diode slit height
radius_photo = 4.1;  //radius of photodiode
radius_photo2 = 3;   //radius of photodiode
radius_photo3 = 4.2; //radius of photodiode
LEDtube_L = 3+16.5;      //height of the tube that holds the LED assembly (W+height LED assembly print - thickness one print)
width_pico4 = 3; //width of Molex Pico-Clasp 4p connector
height_pico4 = 5;//height of Molex Pico-Clasp 4p connector
width_pico6  = 5; //width of Molex Pico-Clasp 6p connector
height_pico6 = 8; //height of Molex Pico-Clasp 6p connector
NTC_t = 1.0;  //Thickness of NTC sensor
NTC_d = 8.5;  //Diameter of NTC sensor
width_NTC = 3;//Width of NTC sensor
height_NTC = NTC_d+1;//Height of NTC sensor


slit_diff=slit2_H-slit1_H; //Help
	  

/* for printing */
coil_shift = coil_r+T+1;// how far out the coils are retracted
show_bottom = true; // Show coil closing rings

// Individual components in one field
if(true){
     //Print area for MarkedForged Onyx (320x132x154mm)
     //color("black") cube([320,132,1],center=true);
     
     // Shift 1: Functional parts
     //translate([10,0,frame_len/2]) frame();
     //translate([-70,30,0]) led_holder();
     //translate([-70,-30,0]) coil(); // need three of those
     //translate([-130,30,0]) coil();
     //translate([-130,-30,0]) top_coil();
     //translate([90,30,0]) coil();
     //translate([90,-30,0]) bottom_coil();
     //translate([140,30,0]) top_lid();
     //translate([140,-30,slit_H+T+slit1_H/2]) cuvette_insert(Wcuv,slit_H);
     translate([0,15,0]) top_lid();
     translate([0,-15,slit_H+T+slit1_H/2]) cuvette_insert(Wcuv,slit_H);

     
     // Shift 2: Coil covers
     xoff = 70;
     //yoff = 30;//For MarkedForged
     yoff = 30 + 60;//For Thingiverse
     //translate([-xoff,-yoff,0]) coil_spindle_bottom();
     //translate([-xoff, yoff,0]) coil_spindle_bottom();
     //translate([0, yoff,0]) coil_spindle_bottom();
     //translate([0,-yoff,0]) coil_spindle_bottom();

     //translate([xoff, yoff,0]) coil_spindle_bottom();
     //translate([xoff,-yoff,0]) coil_spindle_bottom();

}


// Generate entire design
if(false){
     difference() // Cut out box to see inside
     {
	  union(){
	       color("black") translate([0,0,0])
		    frame();
	       color("blue") translate([0,0,0])
		    cuvette_insert(Wcuv,slit_H);
	       translate([coil_shift,0,0]) rotate([0,90,0])
		    led_holder();
	       translate([0,0,coil_shift])
		    top_coil()  ; //top coil (with lid hole)
	       translate([0,0,-coil_shift]) rotate([180,0,0])
		    bottom_coil(); //bottom coil (with hole for mounting)
	       translate([0,-coil_shift,0]) rotate([90,0,0])
	       	    coil();  // NTC
	       translate([0,+coil_shift,0]) rotate([-90,0,0])
	       	    coil();  // scatter
	       translate([-coil_shift,0,0]) rotate([0,-90,0])
	       	    coil(); //photo-diode
	       translate([0,0,60])    top_lid();
	  }
	  translate([0,0,-90])
	       cube([150,150,180],center=false);
     }
}


//inspect frame with cross-section:
/* difference() */
/* { */
/*      union() */
/* 	  { */
/* 	       frame(); */
/* 	       //translate([0,0,-slit_H]) */
/* 	       //cuvette_insert(); */
/* 	  } */
/*      translate([-50,-50,-50]) */
/*      //translate([-50,-50,-50]) */
/* 	  cube([100,50,100],center=false); */
/* } */



// frame (center part)
module frame(){
     union(){
	  coil_frame(frame_len);
	  cuvette_holder();
     }
}

// Coil with led holder
module led_holder(){
     union(){
	  coil_spindle(lid=false);
	  //add LED holder tube
	  translate([0,0,LEDtube_L/2+coil_w+T])
	       union(){
	       //create extension tubes
	       cylinder_hollow(LEDtube_L, coil_r-2*T, coil_r-3*T, true);
	       //backsidelid of extension tube
	       translate([0, 0, LEDtube_L/2-T/2])
		    cylinder(h=T, r1=coil_r-2*T, r2=coil_r-2*T,
			     center=true);
	       //frontside rim to attach to coil_spindle
	       translate([0,0,-LEDtube_L/2+T/2])
		    cylinder_hollow(T,coil_r-T/2-play,coil_r-2*T,true);
	  }
     }
}//end module ledholder

// Coil on top with opening for lid
module top_coil(){
     coil_spindle(lid=false);
}

/* Coil on bottom with hole for fixation entire frame. It extends a little to make room for the coil wires and has a 4 mm hole to fix the entire measurement head */
module bottom_coil(){
     difference(){
	  union(){
	       coil_spindle(lid=true);
	       t=1;
	       translate([0,0,coil_w+2*T+t/2]){
		    cylinder(h=t, r1=coil_r-T/2-play, r2=coil_r-T/2-play, center=true);
	       }
	  }
	  cylinder(h=100,r1=2,r2=2,center=true);//hole for mounting
     }
}
     
// Coil with no special function
module coil(){
     coil_spindle();
}


/* Cuvette insert */
/* Designed to have different inserts for differen cuvette sizes Wcuv and
 different distances between bottom insert and photodiode slits slit_H*/
// Wcuv: space left for the cuvette. The Hellma are 12.4 mm.
// Slit_H
module cuvette_insert(Wcuv,slit_H) {
     radius=hex_r-T;
     difference()
     {
	  translate([-WcuvOut/2, -WcuvOut/2, -radius+T])
	  {/*Hollow cube with inner ridge Wcuv and with bottom */
	       /* such that distance to center of slits is slit_H */
	       difference(){
		    cube([WcuvOut, WcuvOut, Hcuv], center=false);

		    /* hollow inside */
		    translate([(WcuvOut-Wcuv)/2,
			       (WcuvOut-Wcuv)/2,
			       radius-T-slit_H])
			 cube([Wcuv, Wcuv, Hcuv+2],
			      center=false);

		    /* text on side */
		    translate([WcuvOut-0.49,WcuvOut/2,Hcuv-3])
			 rotate([90,0,90])
			 textemboss(str(Wcuv));
		    translate([0.49,WcuvOut/2,Hcuv-3])
			 rotate([90,0,-90])
			 textemboss(str(slit_H));

		    /* small holes for easy removal */
		    translate([Wcuv/2+T/2,0,Hcuv-4])
			 rotate([90,0,0])
			 cylinder(h=2*T,r1=1,r2=1,center=true);
		    translate([Wcuv/2+T/2,Wcuv,Hcuv-4])
			 rotate([90,0,0])
			 cylinder(h=2*T,r1=1,r2=1,center=true);
	       }		    
	  }
	  union(){
	       // LED slit (entry for light)
	       translate([Wcuv/2, 0 ,0])
		    cube([2*T+1, slit1_W+play,
			  slit1_H+play], center=true);
	       //Photodiode slit
	       translate([-Wcuv/2-T/2,0, slit1_H/2+slit_diff/2])
		    translate([1, 0, -slit2_dist/2])
		    cube([T+1, slit2_W+play, slit2_H+play], center=true);
	       //Scatter diode slit
	       translate([0, (Wcuv/2+1.5*T)-1 ,0])
		    rotate([90,90,0])
		    cylinder(h=3*T, r1=radius_photo2+play,
			     r2=radius_photo2+play, center=true);
	  }
     }
}

module top_lid(){
     top_lid_height = 15; //Increase to accommodate for cuvette with plug
     translate([0,0,top_lid_height])
     	  union(){
     	       polyN(8, T, coil_r-T);
     	       translate([0,0,-top_lid_height/2])
     	       	    hex_hollow(top_lid_height, hex_r-2*T-play/2,
     	       		       hex_r-3*T-play/2);
	       knob();
     }
}
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

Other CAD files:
HousingCAD/CoilHousing/bottom.dxf
HousingCAD/InstrumentHousing/TFTHolder.stl
3D_designs/Design_v4_Hans/components/stl_files/design_v4_Hans_frame.stl
3D_designs/Design_v7/MagOD_v7_compenents.stl
HousingCAD/InstrumentHousing/TFTHolder.scad
3D_designs/Design_v4_Hans/components/open_scad/design_v4_Hans_coil_open.scad
3D_designs/Design_v4_Hans/components/open_scad/design_v4_Hans_coils.scad
3D_designs/Design_v4_Hans/components/open_scad/design_v4_Hans_cuvette.scad
3D_designs/Design_v4_Hans/components/open_scad/design_v4_Hans_frame.scad
3D_designs/Design_v4_Hans/components/open_scad/design_v4_Hans_ledholder.scad
3D_designs/Design_v4_Hans/components/open_scad/design_v4_Hans_toplid.scad
3D_designs/Design_v4_Hans/components/stl_files/design_v4_Hans_ledholder.stl
3D_designs/Design_v4_Hans/components/stl_files/design_v4_Hans_toplid.stl
3D_designs/Design_v5/components/coil_4_pieces.stl
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

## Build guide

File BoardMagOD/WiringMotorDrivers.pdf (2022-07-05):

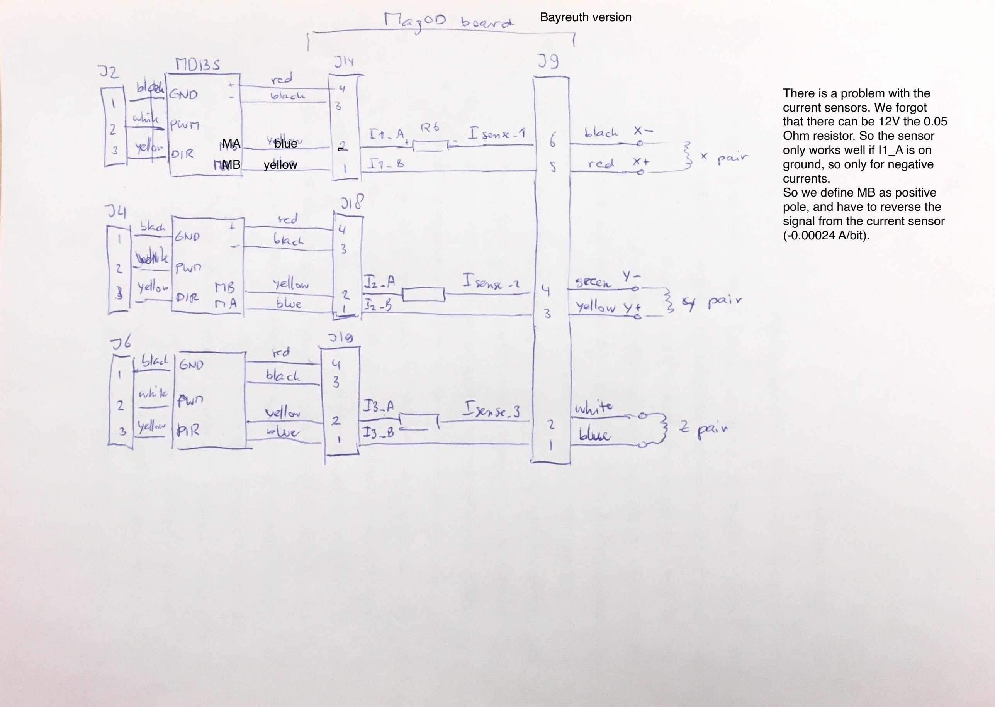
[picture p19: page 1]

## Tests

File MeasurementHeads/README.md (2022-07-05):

# Measurement head electronics
photoDiode : photodetector
refPhotoDiode: board to holde RBG led/LED-mono module and reference photodiode
RGBLed: RGB Led module
LED_mono: Monochrome led module

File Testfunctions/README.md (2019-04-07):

# Testfunctions
Leon Abelmann, 7 April 2019
Programs to test the various subsystems of the MagOD boards:
MAGOD1: Version with Arduino MEGA and ST7735 1.8" 128x160 screen with joystick button
MAGOD2: Version with ESP32 Devkit and TFTM050 5" 480x272 screen and
 capacitive touch

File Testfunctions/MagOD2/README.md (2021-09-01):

# MagOD2 Testfunctions
Leon Abelmann

Calibration programs
TestTFT50/ts_calibration: Calibrate touch screen
TestCurrentCalibration:  Calibrate PWM to current sensors and field if
you have Hall sensor

Programs to test the various subsystems of the MagOD2 boards:

TestADC: Test the two ADC1115 AD converters

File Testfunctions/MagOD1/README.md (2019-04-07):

# MagOD1 Testfunctions
Leon Abelmann, 7 April 2019

Programs to test the various subsystems of the MagOD2 boards:

Cardinfo: Test the functionalite of the SD card reader

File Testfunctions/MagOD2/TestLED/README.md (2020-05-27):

# TestLED.ino
Leon Abelmann, April 2020
Toggle the led colors red green blue pauze, 1 sec interval ...
No screen output

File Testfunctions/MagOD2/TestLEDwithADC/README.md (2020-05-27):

# TestLEDWithADC.ino
Leon Abelmann, April 2020
Change PWM of LEDs in all colours and record the signal from the photodiode and
reference photodiode.

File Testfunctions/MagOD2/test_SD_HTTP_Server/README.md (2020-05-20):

# SD HTTP WebServer
Rob Kräwinkel, 20 May 2020

Program to try out an implementation of a HTTP webserver on the second core of the ESP32 microcontroller

Files and folders can be read, downloaded, created and deleted from the SD card through a internet browser using simple commands:

To read or download: http://esp32sd.local/folder or http://esp32sd.local/folder/file.txt or http://esp32sd.local/folder/file.txt?download=1

To delete: http://esp32sd.local/folder?delete=1 or http://esp32sd.local/folder/file.txt?delete=1

To create: http://esp32sd.local/folder?create=1 or http://esp32sd.local/folder/file.txt?create=1

Uploading a file is a bit harder as the internet browser can only send HTTP GET commands and not HTTP PUSH commands which are required for file uploading. The program curl can be used for this fairly simply (python could be used as well)

To upload: curl -F "data=@fileToUpload.txt" -X POST http://esp32sd.local/edit?dir=/folder/fileToUpload.txt

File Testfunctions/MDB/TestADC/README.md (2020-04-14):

# TestADC.ino
Leon Abelmann, April 2020

Program to test the ADS1115 converters on the MagOD2 board.
Will read the ADC values, send them to the serial port and display
them on the TFTM50 screen. Calculates the standard deviation of N
measurements, and max-min values (only serial output).

Requires MagOD_ADS115, which is a modification of the Adafruit ADS1015
library to incorporate interupt based readout. You can set the
samplingrate (sampleRate).

ADC0 is read using interupt on port 13 of ESP32 (connected to
ALERT/RDY pin of ADS1115)

ADC1 is read using a suitable delay.

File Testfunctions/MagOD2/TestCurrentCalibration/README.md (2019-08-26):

# TestFieldWithADC.ino
Leon Abelmann, Jun 2019
Program to test the PWM ports that set the field. You can program the
PWM values per channel. The ADC converter outputs on the measurement
resistors are displayed

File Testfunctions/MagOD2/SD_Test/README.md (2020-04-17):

SD_Test
Leon Abelmann, April 2020
Test SD card functionality. Only serial port ouput, no TFT.
Make sure the micro SD card is formatted correctly:
- Format MSDOS(FAT)
- Scheme "Master Boot Record"

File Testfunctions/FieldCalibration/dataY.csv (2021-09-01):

2021-07-22 17:11:57:144781 | 0.0005816393 | 0.00019 | 5e-05 | 0.00038
2021-07-22 17:11:57:774620 | 0.0005852588 | -4e-05 | 0.00018 | 0.00017
2021-07-22 17:11:58:404573 | 0.0005813851 | -0.00016 | 7e-05 | 0.00026
2021-07-22 17:11:59:044175 | 0.0005578024 | -2e-05 | 5e-05 | 0.00017
2021-07-22 17:11:59:694316 | 0.0005859436 | -4e-05 | 0.00022 | 0.00017
2021-07-22 17:12:00:324409 | 0.0005642589 | -2e-05 | 0.00011 | 0.00026
2021-07-22 17:12:00:964339 | 0.0005816066 | -2e-05 | -8e-05 | 0.00017
2021-07-22 17:12:01:594617 | 0.0005760632 | -2e-05 | -0.0 | 0.00027
2021-07-22 17:12:02:233912 | 0.000584077 | -5e-05 | 0.00022 | 0.00031
2021-07-22 17:12:02:874069 | 0.0005766032 | 0.00015 | 0.00011 | 0.0002
2021-07-22 17:12:03:503886 | 0.0005704936 | -9e-05 | 0.00011 | 0.00026
2021-07-22 17:12:04:143634 | 0.0005772512 | -4e-05 | -2e-05 | -5e-05
2021-07-22 17:12:04:783889 | 0.0005870197 | 0.00012 | -0.0001 | 0.0004
2021-07-22 17:12:05:433072 | 0.0005914218 | -5e-05 | -0.00013 | -2e-05
2021-07-22 17:12:06:073587 | 0.0005734388 | -4e-05 | 7e-05 | 0.0002
2021-07-22 17:12:06:713296 | 0.0005838892 | 0.00013 | -2e-05 | 0.00026
2021-07-22 17:12:07:353316 | 0.0005713736 | 0.0002 | 5e-05 | 0.00015
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

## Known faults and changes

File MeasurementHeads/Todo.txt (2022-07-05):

 Fixes:

Improvements:
1. A LED might be more stable than a diode for voltage offset
2. There are better connectors
3. The OPA140 is difficult to obtain. Alternative?
4. J2 on LED board connects to J1 on refDiode board. Confusing..
5. The connectors on the refDiode board are mirrored
6. It would be nicer if the connector to the led and refDiode board would be on the LED side.
7. More space between the resistors and the led on the led board.

8. The refDiode board is too big, remove 0.5 mm from all sides.
9. The silk screen on the photodiode board has the wrong image for BPW21.		

MagOD2 board
D32 LED-Green
D2 LED-Red  (Pull-up/down for boot)
RX2 LED-Blue
TX2 INT

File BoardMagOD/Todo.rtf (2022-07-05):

If we supply the ADC1115 with 5 V, we can use the full swing of the pre-amps. Needs logic converters. Maybe too much for the small improvement.

Melixis 3 axis Hall sensor with temperature is only 10 Euro:

https://github.com/tjhowse/melexis_interface/blob/master/melexis.cpp

TODO in program:
- Schrijf langs de verticale as wat we plotten
- Misschien grafiek even langs als 1 run

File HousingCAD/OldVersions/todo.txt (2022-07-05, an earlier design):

Fixes:

Improvements:
We could build around a hexagon premade structure.
https://nl.aliexpress.com/item/32mm-ID-6-Way-PVC-Buis-Gezamenlijke-Pijp-Adapter-Water-Connector-Voor-Tuin-Irrigatie-Systeem-DIY/32854499448.html

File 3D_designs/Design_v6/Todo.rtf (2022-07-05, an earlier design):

Cuvette holders with different inner diameters
Cuvette holder for MC-1 speed

Better support for wires coils
Holes in coil holders could be central

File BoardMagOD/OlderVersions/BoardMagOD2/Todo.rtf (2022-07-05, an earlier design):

1. Pin-out ESP32, port 34/35 cannot be used for output
D32 LED-Green
D2 LED-Red (Pull-up/down for boot)
RX2 LED-Blue
TX2 INT

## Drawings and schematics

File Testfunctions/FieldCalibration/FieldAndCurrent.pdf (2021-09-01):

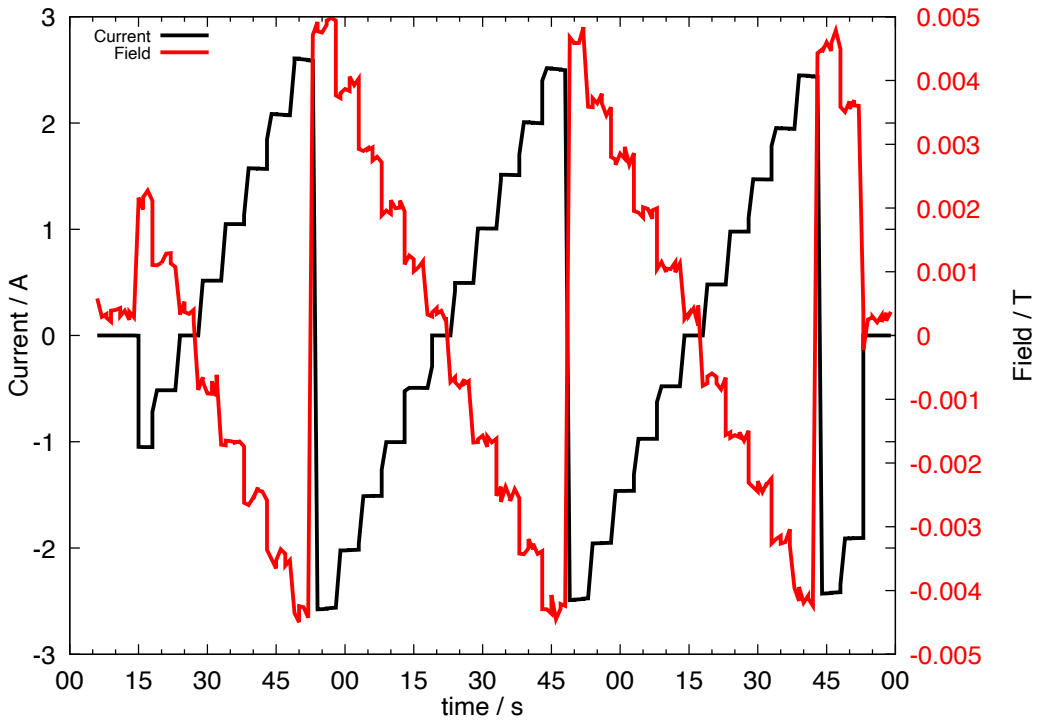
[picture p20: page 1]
Current / A; Field / T; time; Current Field

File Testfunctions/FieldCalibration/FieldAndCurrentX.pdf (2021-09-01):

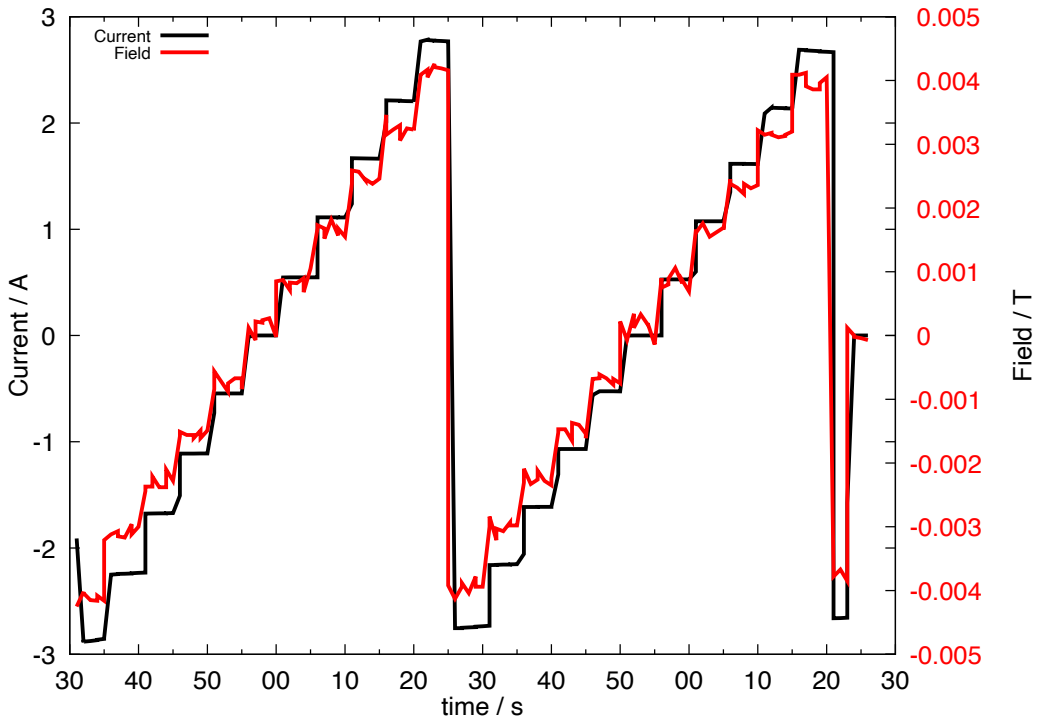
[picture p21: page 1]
Current / A; Field / T; time; Current Field

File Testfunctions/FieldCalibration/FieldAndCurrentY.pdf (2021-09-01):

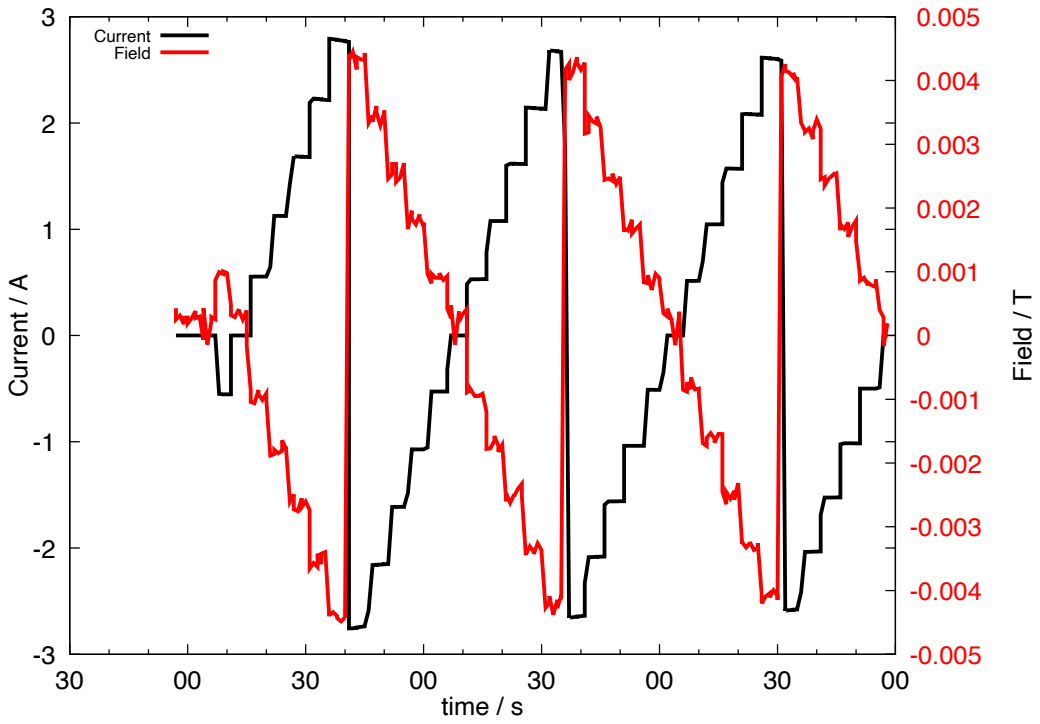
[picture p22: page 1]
Current / A; Field / T; time; Current Field

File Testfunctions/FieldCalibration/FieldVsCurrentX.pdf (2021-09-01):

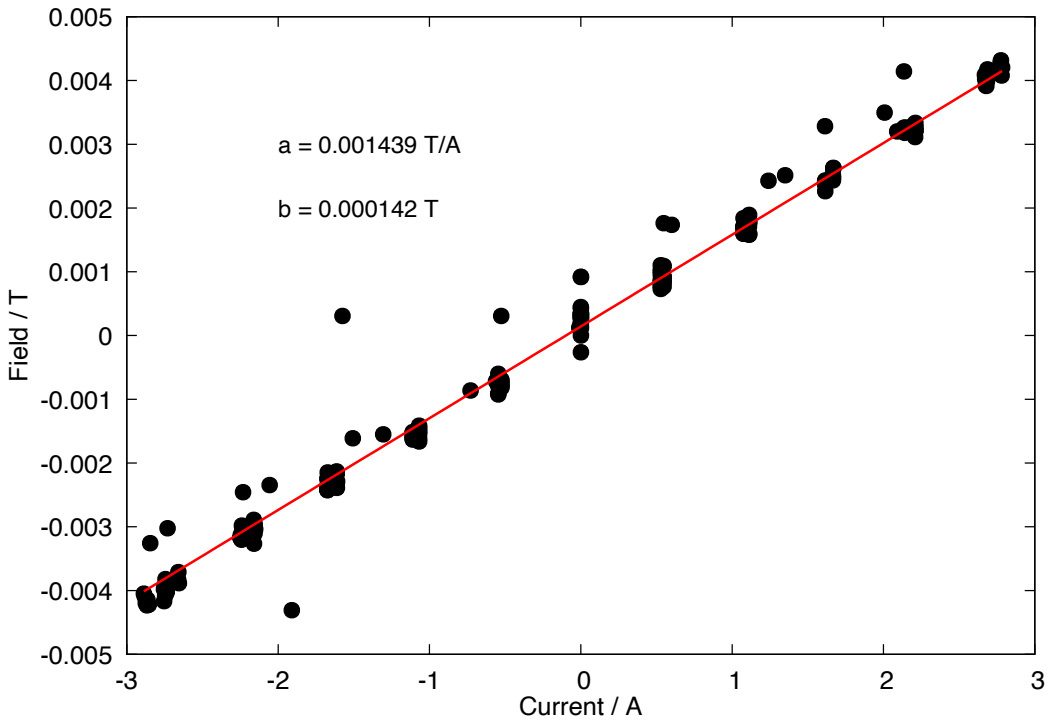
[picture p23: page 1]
Field / T; Current

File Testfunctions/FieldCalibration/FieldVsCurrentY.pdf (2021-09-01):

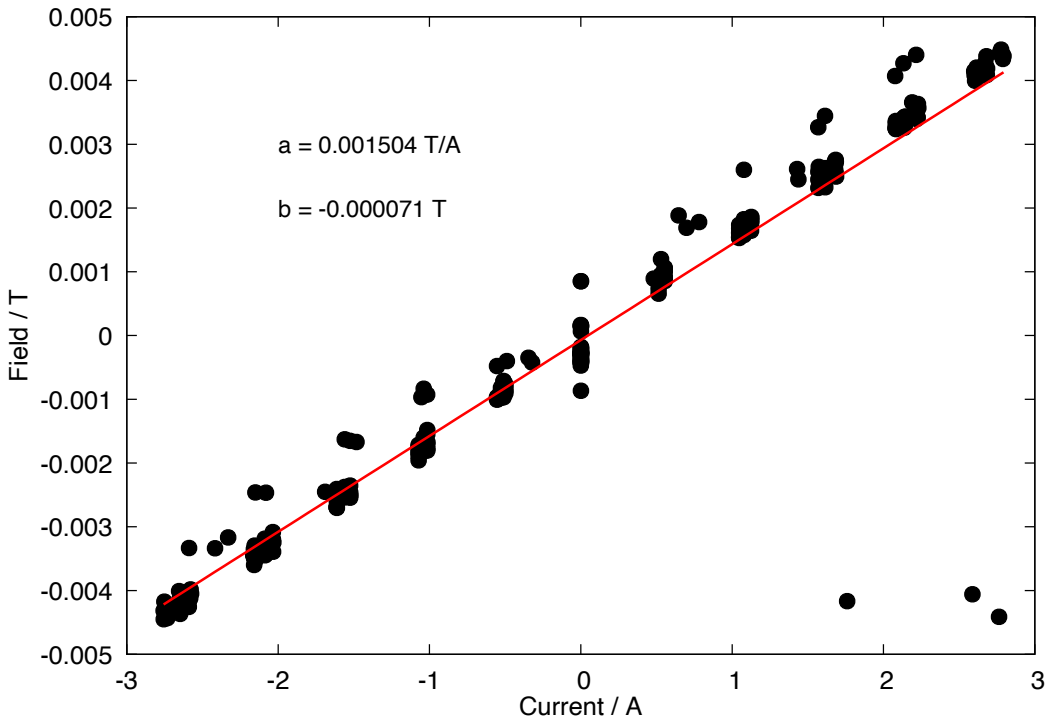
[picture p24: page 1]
Field / T; Current / A

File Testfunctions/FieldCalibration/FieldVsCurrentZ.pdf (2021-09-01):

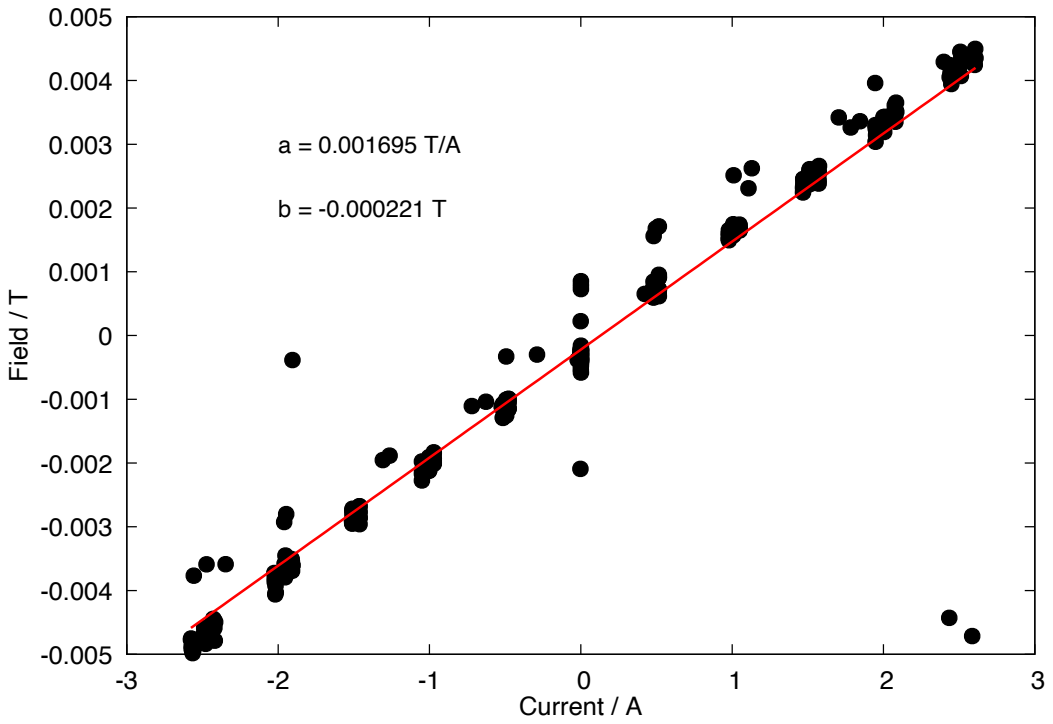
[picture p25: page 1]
Field / T; Current / A

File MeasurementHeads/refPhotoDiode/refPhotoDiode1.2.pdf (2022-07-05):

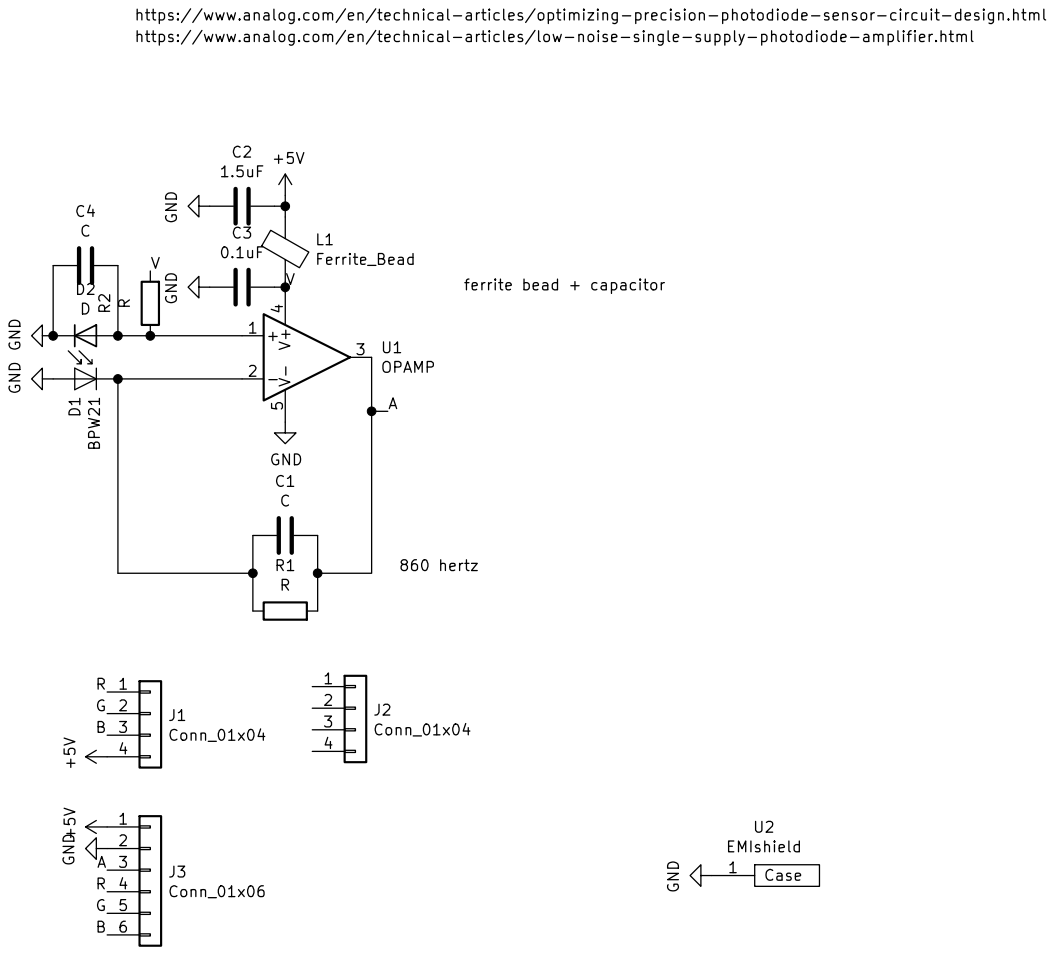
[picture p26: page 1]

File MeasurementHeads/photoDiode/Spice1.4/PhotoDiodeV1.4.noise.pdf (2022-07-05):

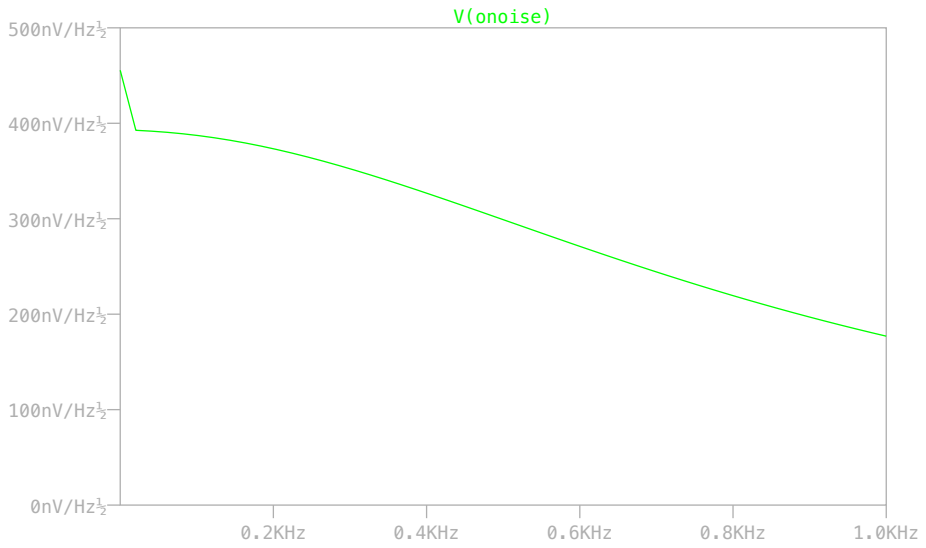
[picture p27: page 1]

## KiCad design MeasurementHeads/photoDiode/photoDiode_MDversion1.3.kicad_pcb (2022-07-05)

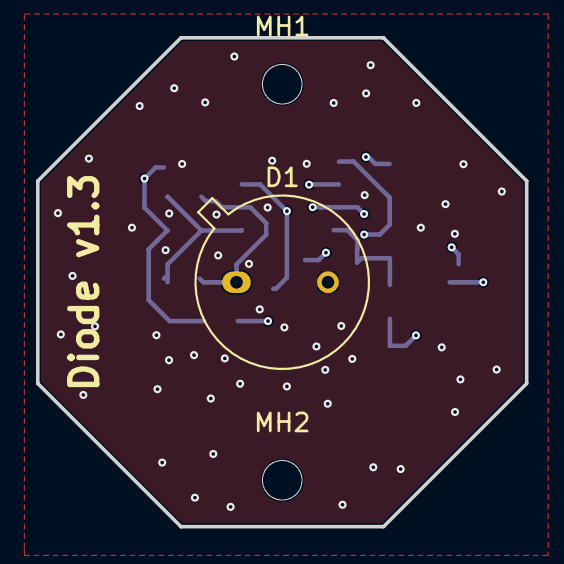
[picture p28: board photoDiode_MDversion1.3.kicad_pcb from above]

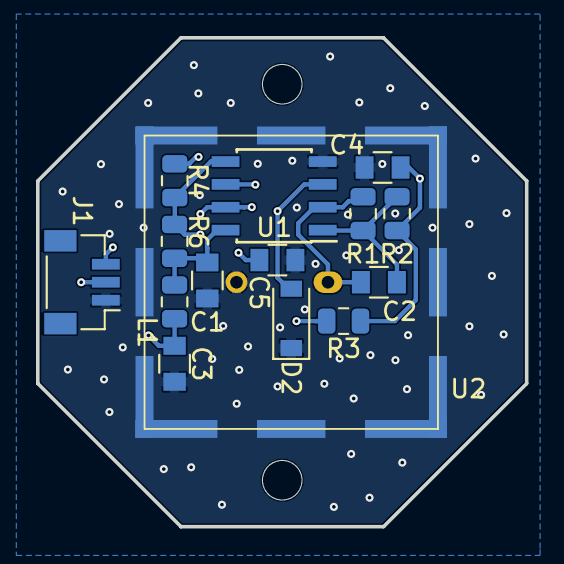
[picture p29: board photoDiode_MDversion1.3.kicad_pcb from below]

Board: 4 copper layers, 27.2 x 27.2 mm, 18 parts (15 on the bottom side), 9 nets.

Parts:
C1: 0.1uF; C_0805
C2, C5: C; C_0805
C3: 1.5uF; C_0805
C4: 47uF; C_0805
D1: BPW21; TO-5-2_Window
D2: D; D_SOD-123
J1: Conn_01x03; Molex_Pico-Clasp_501331-0307_1x03-1MP_P1.00mm_Vertical
L1: Ferrite_Bead; L_0805_2012Metric
MH1, MH2: MountingHole; MountingHole_2.2mm_M2
R1, R3, R4, R6: R; R_0805_2012Metric
R2: 3; R_0805_2012Metric
U1: Opamp_Dual_Generic; SOIC-8_3.9x4.9mm_Pitch1.27mm
U2: EMIshield; Laird-BMI-S-202-F

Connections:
+5V: C3.2, J1.2, L1.1
/A: J1.3, R3.2, U1.7
/Ref1: D2.2, R4.1, U1.3
/Ref2: C5.2, R4.2, R6.1, U1.5
/Vdd: C1.1, L1.2, R6.2, U1.8
GND: C1.2, C3.1, C4.2, C5.1, D1.2, D2.1, J1.1, U1.4, U2.1
unnamed: C2.1, R1.2, R2.1, U1.1
unnamed: C2.2, D1.1, R1.1, U1.2
unnamed: C4.1, R2.2, R3.1, U1.6

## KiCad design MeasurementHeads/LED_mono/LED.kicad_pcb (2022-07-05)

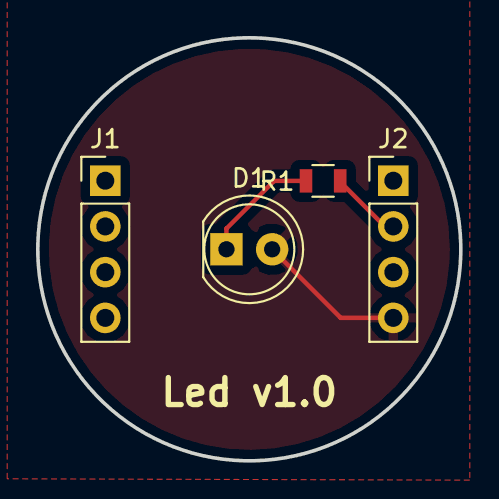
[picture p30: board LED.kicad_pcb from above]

Board: 2 copper layers, 23.5 x 23.5 mm, 4 parts (0 on the bottom side), 3 nets.

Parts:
D1: LED; LED_D5.0mm
J1, J2: Conn_01x04; Socket_Strip_Straight_1x04_Pitch2.54mm
R1: R; R_0805

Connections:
+5V: D1.2, J2.4
/G: J2.2, R1.2
unnamed: D1.1, R1.1

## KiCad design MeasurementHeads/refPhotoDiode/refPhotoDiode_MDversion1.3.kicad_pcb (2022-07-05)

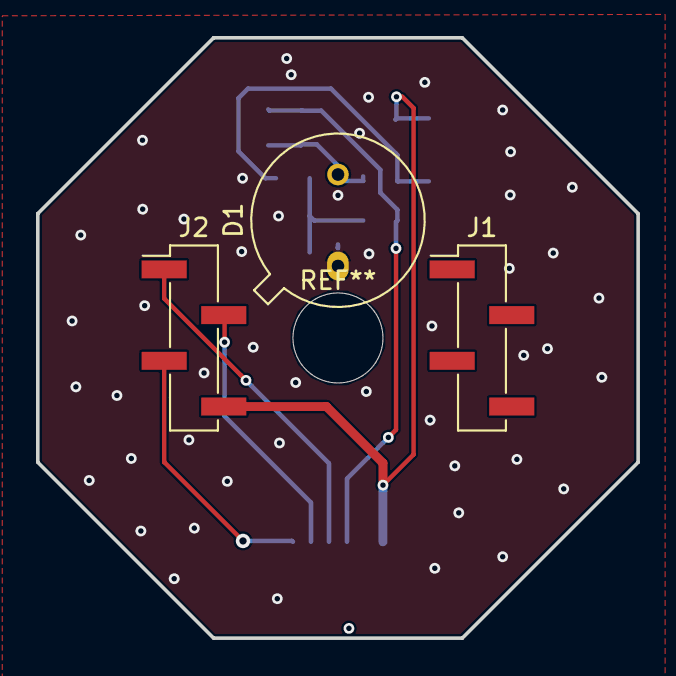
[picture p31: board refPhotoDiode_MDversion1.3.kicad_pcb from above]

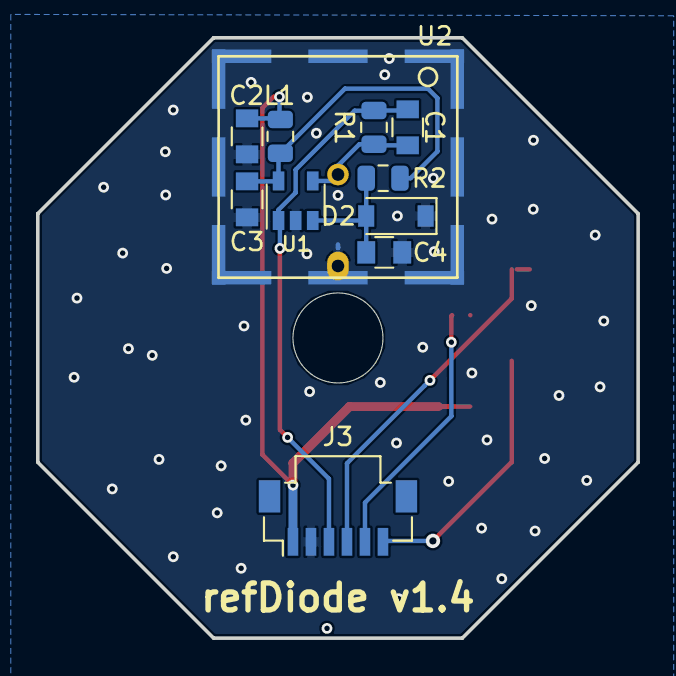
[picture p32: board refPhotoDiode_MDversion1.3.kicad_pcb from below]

Board: 2 copper layers, 33.4 x 33.4 mm, 14 parts (11 on the bottom side), 9 nets.

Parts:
C1: 180p; C_0805
C2: 1.5uF; C_0805
C3: 0.1uF; C_0805
C4: 1u; C_0805
D1: BPW21; TO-5-2_Window
D2: D; D_SOD-123
J1, J2: Conn_01x04; PinHeader_1x04_P2.54mm_Vertical_SMD_Pin1Left
J3: Conn_01x06; Molex_Pico-Clasp_501331-0607_1x06-1MP_P1.00mm_Vertical
L1: Ferrite_Bead; L_0805_2012Metric
R1: 1000k; R_0805_2012Metric
R2: 20k; R_0805_2012Metric
U1: OPA140; SOT-23-5
U2: EMIshield; Wurth-3610213126S-EMIshield-13.26x12.3mm

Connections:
+5V: C2.1, J2.4, J3.1, L1.1
/A: C1.1, J3.3, R1.2, U1.1
/B: J2.3, J3.6
/G: J2.2, J3.5
/R: J2.1, J3.4
/V: C3.1, L1.2, R2.2, U1.5
GND: C2.2, C3.2, C4.2, D1.2, D2.1, J3.2, U1.2, U2.1
unnamed: C1.2, D1.1, R1.1, U1.4
unnamed: C4.1, D2.2, R2.1, U1.3

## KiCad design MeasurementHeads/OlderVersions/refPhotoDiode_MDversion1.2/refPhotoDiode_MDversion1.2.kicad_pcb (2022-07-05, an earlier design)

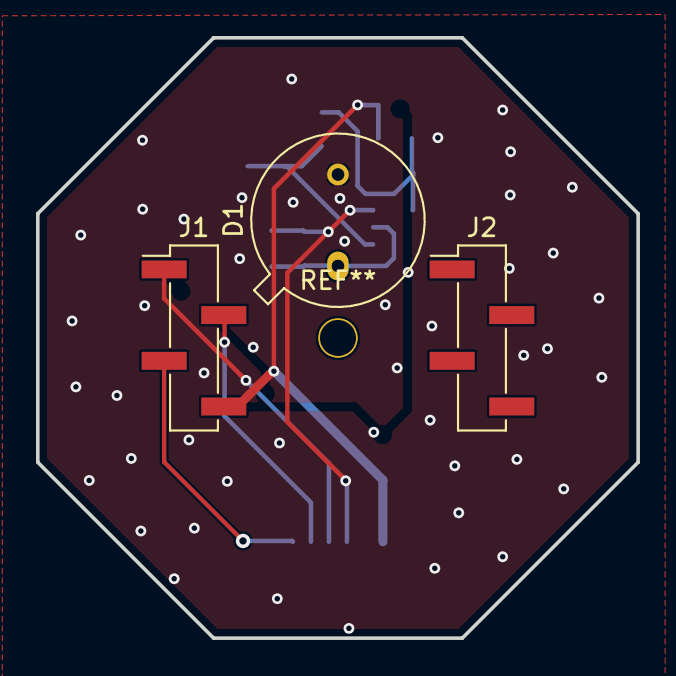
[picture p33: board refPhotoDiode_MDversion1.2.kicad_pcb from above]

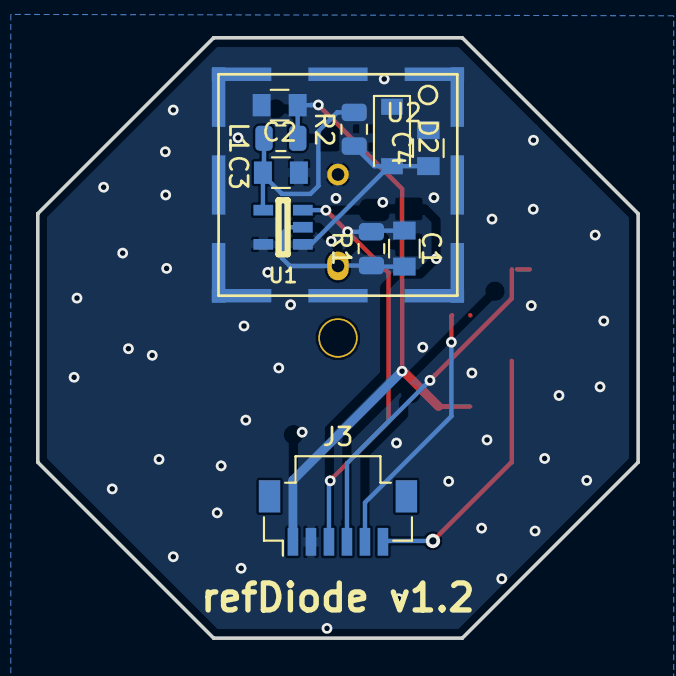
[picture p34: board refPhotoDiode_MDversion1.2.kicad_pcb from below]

Board: 2 copper layers, 33.4 x 33.4 mm, 14 parts (11 on the bottom side), 9 nets.

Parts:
C1, C4: C; C_0805
C2: 1.5uF; C_0805
C3: 0.1uF; C_0805
D1: BPW21; TO-5-2_Window
D2: D; D_SOD-123
J1, J2: Conn_01x04; PinHeader_1x04_P2.54mm_Vertical_SMD_Pin1Left
J3: Conn_01x06; Molex_Pico-Clasp_501331-0607_1x06-1MP_P1.00mm_Vertical
L1: Ferrite_Bead; L_0805_2012Metric
R1, R2: R; R_0805_2012Metric
U1: OPAMP; SOT-23-5
U2: EMIshield; Wurth-3610213126S-EMIshield-13.26x12.3mm

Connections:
+5V: C2.1, J1.4, J3.1, L1.1
/A: C1.1, J3.3, R1.2, U1.3
/B: J1.3, J3.6
/G: J1.2, J3.5
/R: J1.1, J3.4
/V: C3.1, L1.2, R2.2, U1.4
GND: C2.2, C3.2, C4.2, D1.2, D2.1, J3.2, U1.5, U2.1
unnamed: C1.2, D1.1, R1.1, U1.2
unnamed: C4.1, D2.2, R2.1, U1.1

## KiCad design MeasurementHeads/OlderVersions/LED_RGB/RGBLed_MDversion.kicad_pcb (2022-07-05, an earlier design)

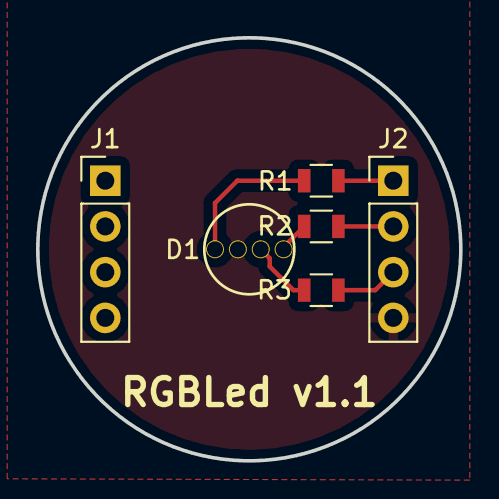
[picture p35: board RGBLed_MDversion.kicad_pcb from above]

Board: 2 copper layers, 23.5 x 23.5 mm, 6 parts (0 on the bottom side), 7 nets.

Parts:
D1: LED_RABG; L-154A4SUREQBFZGEW
J1, J2: Conn_01x04; Socket_Strip_Straight_1x04_Pitch2.54mm
R1, R2, R3: R; R_0805

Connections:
+5V: D1.2, J2.4
/B: J2.3, R3.2
/G: J2.2, R2.2
/R: J2.1, R1.2
unnamed: D1.1, R1.1
unnamed: D1.3, R3.1
unnamed: D1.4, R2.1

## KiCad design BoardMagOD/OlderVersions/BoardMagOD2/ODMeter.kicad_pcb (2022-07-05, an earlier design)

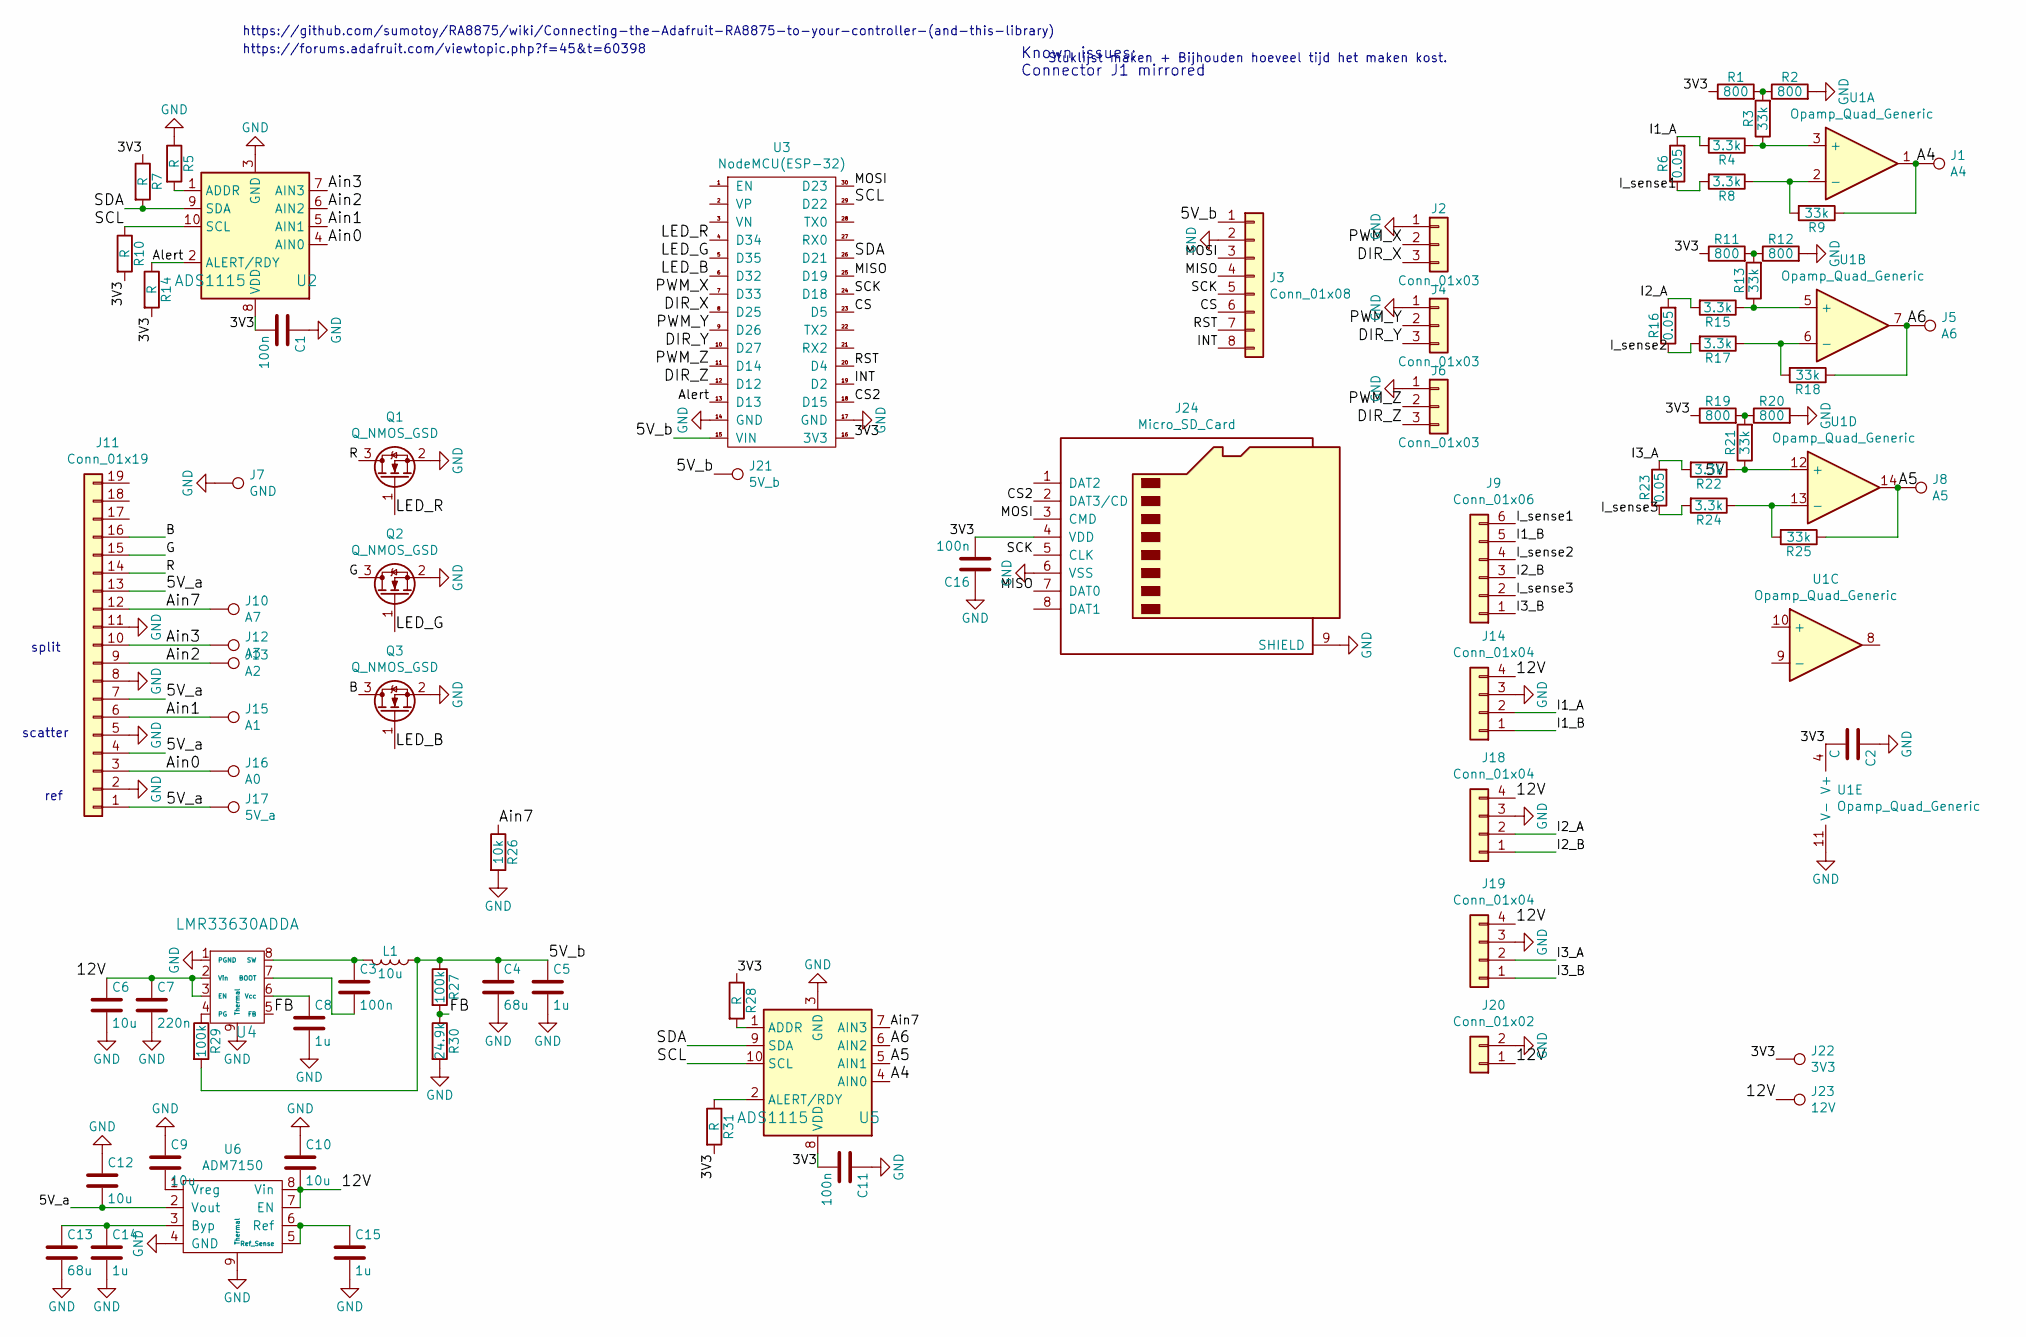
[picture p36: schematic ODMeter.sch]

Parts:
C1, C3, C11, C16: 100n; C_0805
C2: C; C_0805
C4, C13: 68u; CP_Tantalum_Case-D_EIA-7343-31_Hand
C5: 1u; C_0805
C6, C9, C10, C12: 10u; C_1210
C7: 220n; C_0805
C8, C14, C15: 1u; C_0603
J1: A4; TestPoint-Harwin-S2761-46R
J2, J4, J6: Conn_01x03; Pin_Header_Straight_1x03_Pitch2.54mm
J3: Conn_01x08; Pin_Header_Straight_1x08_Pitch2.54mm
J5: A6; TestPoint-Harwin-S2761-46R
J7: GND; TestPoint-Harwin-S2761-46R
J8: A5; TestPoint-Harwin-S2761-46R
J9: Conn_01x06; KK41791_straight1x6
J10: A7; TestPoint-Harwin-S2761-46R
J11: Conn_01x19; HDMI-RightAngle-47151-1051
J12: A3; TestPoint-Harwin-S2761-46R
J13: A2; TestPoint-Harwin-S2761-46R
J14, J18, J19: Conn_01x04; KK41791_straight1x4
J15: A1; TestPoint-Harwin-S2761-46R
J16: A0; TestPoint-Harwin-S2761-46R
J17: 5V_a; TestPoint-Harwin-S2761-46R
J20: Conn_01x02; KK396RPC171813_Straight_1x2
J21: 5V_b; TestPoint-Harwin-S2761-46R
J22: 3V3; TestPoint-Harwin-S2761-46R
J23: 12V; TestPoint-Harwin-S2761-46R
J24: Micro_SD_Card; MicroSd_Wurth_693072010801
L1: 10u; ssr1260
Q1, Q2, Q3: Q_NMOS_GSD; SOT-23
R1, R2, R11, R12, R19, R20: 800; R_0805
R3, R9, R13, R18, R21, R25: 33k; R_0805
R4, R8, R15, R17, R22, R24: 3.3k; R_0805
R5, R7, R10, R14, R28, R31: R; R_0805
R6, R16, R23: 0.05; OAR3
R26: 10k; R_0805
R27, R29: 100k; R_0805
R30: 24.9k; R_0805
U1: Opamp_Quad_Generic; SOIC-14_3.9x8.7mm_P1.27mm
U2, U5: ADS1115; VSSOP-10_3.1x3.1mm_Pitch0.5mm
U3: NodeMCU(ESP-32)
U4: LMR33630ADDA; HSOIC-8
U6: ADM7150; HSOIC-8

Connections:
/3V3: C1.2, C2.2, C11.2, C16.2, J22.1, J24.4 (VDD), R1.1, R7.1, R10.2, R11.1, R14.2, R19.1, R28.1, R31.2, U1.4 (V+), U2.8 (VDD), U3.16 (3V3), U5.8 (VDD)
/5V_a: C12.2, J11.1, J11.4, J11.7, J11.13, J17.1, U6.2 (Vout)
/5V_b: C4.1, C5.1, J3.1, J21.1, L1.1, R27.1, R29.2, U3.15 (VIN)
/12V: C6.1, C7.1, C10.2, J14.4, J18.4, J19.4, J20.1, J23.1, U4.2 (Vin), U4.3 (EN), U6.7 (EN), U6.8 (Vin)
/A4: J1.1, R9.1, U1.1, U5.4 (AIN0)
/A5: J8.1, R25.1, U1.14, U5.5 (AIN1)
/A6: J5.1, R18.1, U1.7, U5.6 (AIN2)
/Ain0: J11.3, J16.1, U2.4 (AIN0)
/Ain1: J11.6, J15.1, U2.5 (AIN1)
/Ain2: J11.9, J13.1, U2.6 (AIN2)
/Ain3: J11.10, J12.1, U2.7 (AIN3)
/Ain7: J10.1, J11.12, R26.1, U5.7 (AIN3)
/Alert: R14.1, U2.2 (ALERT/RDY), U3.13 (D13)
/B: J11.16, Q3.3 (D)
/CS: J3.6, U3.23 (D5)
/CS2: J24.2 (DAT3/CD), U3.18 (D15)
/DIR_X: J2.3, U3.8 (D25)
/DIR_Y: J4.3, U3.10 (D27)
/DIR_Z: J6.3, U3.12 (D12)
/FB: R27.2, R30.1, U4.5 (FB)
/G: J11.15, Q2.3 (D)
/I1_A: J14.2, R4.2, R6.2
/I1_B: J9.5, J14.1
/I2_A: J18.2, R15.2, R16.2
/I2_B: J9.3, J18.1
/I3_A: J19.2, R22.2, R23.2
/I3_B: J9.1, J19.1
/INT: J3.8, U3.19 (D2)
/I_sense1: J9.6, R6.1, R8.2
/I_sense2: J9.4, R16.1, R17.2
/I_sense3: J9.2, R23.1, R24.2
/LED_B: Q3.1 (G), U3.6 (D32)
/LED_G: Q2.1 (G), U3.5 (D35)
/LED_R: Q1.1 (G), U3.4 (D34)
/MISO: J3.4, J24.7 (DAT0), U3.25 (D19)
/MOSI: J3.3, J24.3 (CMD), U3.30 (D23)
/PWM_X: J2.2, U3.7 (D33)
/PWM_Y: J4.2, U3.9 (D26)
/PWM_Z: J6.2, U3.11 (D14)
/R: J11.14, Q1.3 (D)
/RST: J3.7, U3.20 (D4)
/SCK: J3.5, J24.5 (CLK), U3.24 (D18)
/SCL: R10.1, U2.10 (SCL), U3.29 (D22), U5.10 (SCL)
/SDA: R7.2, U2.9 (SDA), U3.26 (D21), U5.9 (SDA)
GND: C1.1, C2.1, C4.2, C5.2, C6.2, C7.2, C8.2, C9.1, C10.1, C11.1, C12.1, C13.2, C14.2, C15.2, C16.1, J2.1, J3.2, J4.1, J6.1, J7.1, J11.2, J11.5, J11.8, J11.11, J14.3, J18.3, J19.3, J20.2, J24.6 (VSS), J24.9 (SHIELD), Q1.2 (S), Q2.2 (S), Q3.2 (S), R2.2, R5.1, R12.2, R20.2, R26.2, R30.2, U1.11 (V-), U2.3 (GND), U3.14 (GND), U3.17 (GND), U4.1 (PGND), U4.9 (Thermal), U5.3 (GND), U6.4 (GND), U6.9 (Thermal)
unnamed: C3.1, L1.2, U4.8 (SW)
unnamed: C3.2, U4.7 (BOOT)
unnamed: C8.1, U4.6 (Vcc)
unnamed: C9.2, U6.1 (Vreg)
unnamed: C13.1, C14.1, U6.3 (Byp)
unnamed: C15.1, U6.5 (Ref_Sense), U6.6 (Ref)
unnamed: R1.2, R2.1, R3.2
unnamed: R3.1, R4.1, U1.3 (+)
unnamed: R5.2, U2.1 (ADDR)
unnamed: R8.1, R9.2, U1.2 (-)
unnamed: R11.2, R12.1, R13.2
unnamed: R13.1, R15.1, U1.5 (+)
unnamed: R17.1, R18.2, U1.6 (-)
unnamed: R19.2, R20.1, R21.2
unnamed: R21.1, R22.1, U1.12 (+)
unnamed: R24.1, R25.2, U1.13 (-)
unnamed: R28.2, U5.1 (ADDR)
unnamed: R29.1, U4.4 (PG)
unnamed: R31.1, U5.2 (ALERT/RDY)

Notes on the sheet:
Stuklijst maken + Bijhouden hoeveel tijd het maken kost.
Known issues: Connector J1 mirrored
ref
scatter
split
https://github.com/sumotoy/RA8875/wiki/Connecting-the-Adafruit-RA8875-to-your-controller-(and-this-library)
https://forums.adafruit.com/viewtopic.php?f=45&t=60398

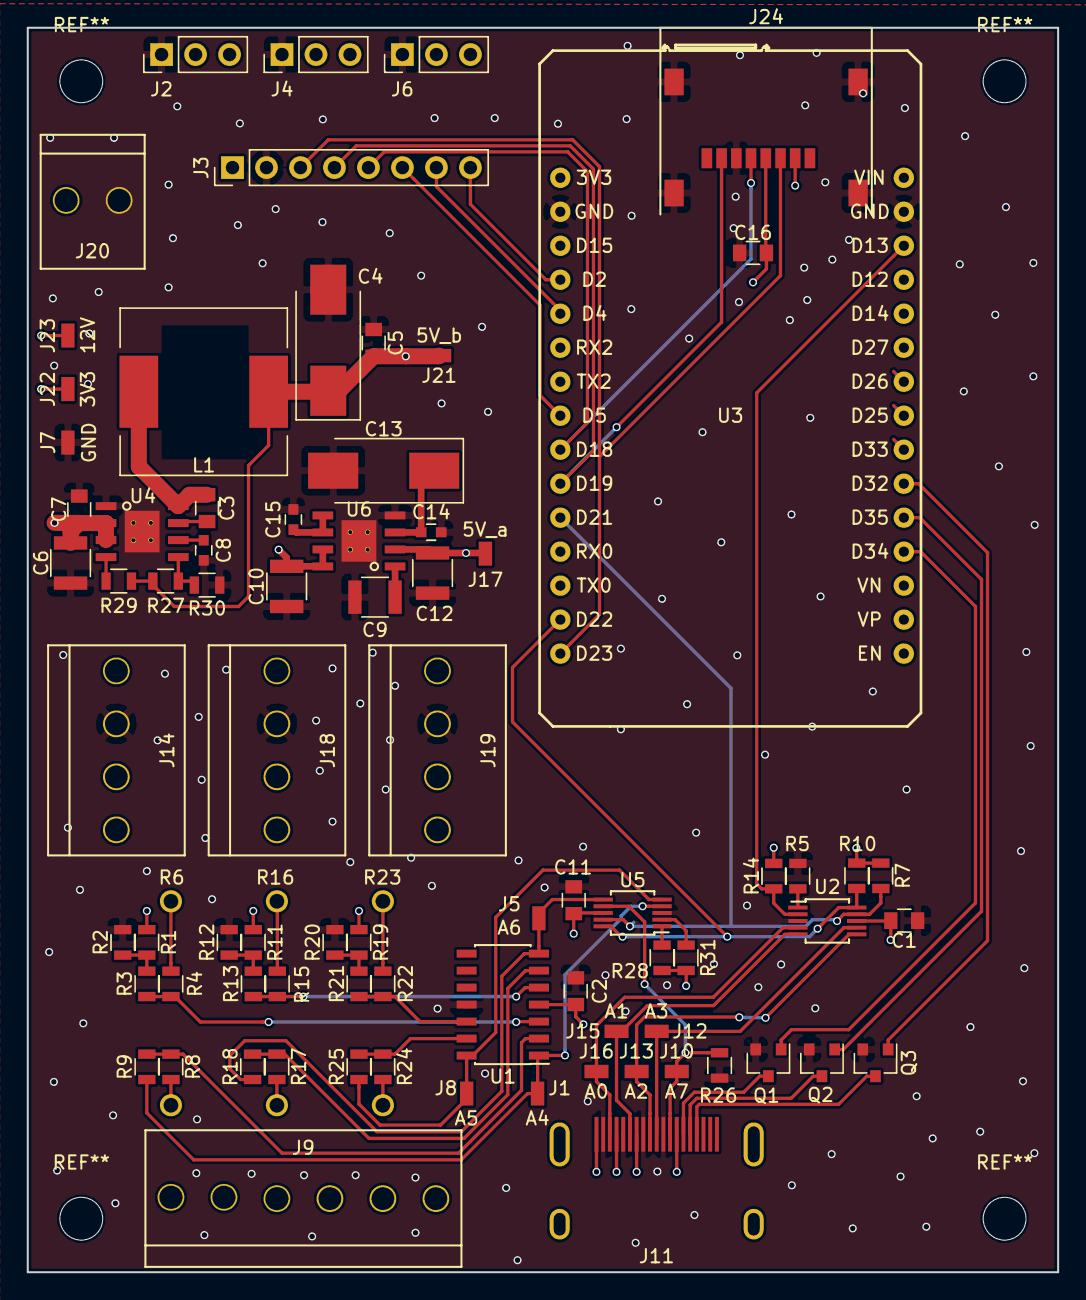
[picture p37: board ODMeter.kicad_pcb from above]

Board: 4 copper layers, 77.0 x 93.0 mm, 81 parts (0 on the bottom side), 64 nets.

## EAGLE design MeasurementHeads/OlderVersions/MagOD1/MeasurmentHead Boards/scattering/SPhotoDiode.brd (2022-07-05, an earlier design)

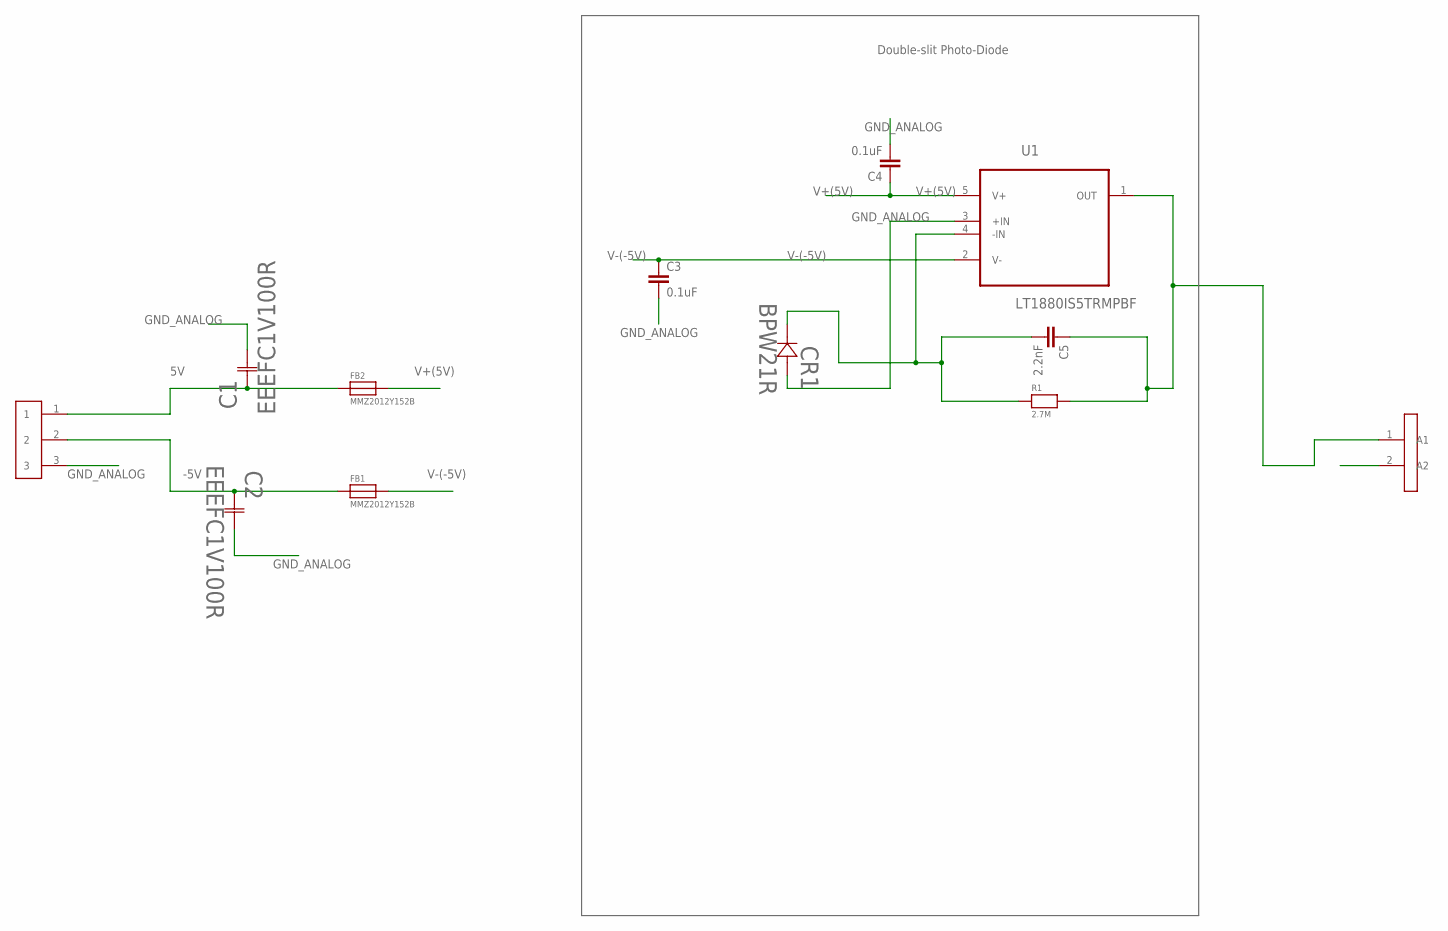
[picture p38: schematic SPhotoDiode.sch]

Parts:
C1, C2: EEEFC1V100R; CAP_EEFC_C
C3, C4: 0.1uF; C0603
C5: 2.2nF; C0603
CR1: BPW21R; TO99_BPW20RF
FB1, FB2: MMZ2012Y152B; 0805
J2: 22-28-8020
R1: 2.7M; 0805
U1: LT1880IS5TRMPBF; SOT95P280X100-5N
U$2: PINHD_SMD-3

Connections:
5V: C1.1 (11), FB2.1, U$2.1
-5V: C2.1 (11), FB1.1, U$2.2
GND_ANALOG: C1.2 (22), C2.2 (22), C3.2, C4.2, CR1.2 (22), J2.2 (A2), U1.3 (+IN), U$2.3
unnamed: C5.1, J2.1 (A1), R1.2, U1.1 (OUT)
unnamed: C5.2, CR1.1 (11), R1.1, U1.4 (-IN)
V+(5V): C4.1, FB2.2, U1.5 (V+)
V-(-5V): C3.1, FB1.2, U1.2 (V-)

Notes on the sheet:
Double-slit Photo-Diode

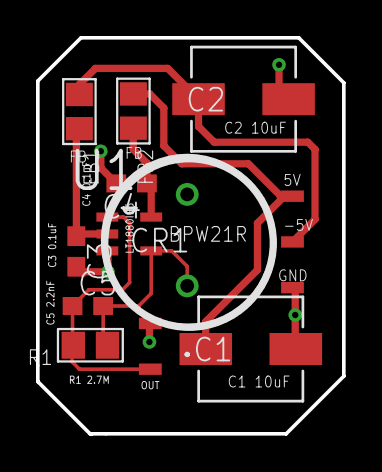
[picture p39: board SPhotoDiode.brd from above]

Board: 2 copper layers, 17.0 x 22.0 mm, 12 parts (0 on the bottom side), 7 nets.

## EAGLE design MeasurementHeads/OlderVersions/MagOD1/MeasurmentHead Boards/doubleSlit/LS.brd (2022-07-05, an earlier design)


Board: 2 copper layers, 19.0 x 26.0 mm, 17 parts (0 on the bottom side), 9 nets.

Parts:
C1, C2: EEEFC1V100R; CAP_EEFC_C
C3, C4: 22nF; C0603
C5, C6, C7, C8: 0.1uF; C0603
FB1, FB2: MMZ2012Y152B; 0805
J2: 22-28-8020
R1, R2: 270k; 0805
U1, U2: LT1880IS5TRMPBF; SOT95P280X100-5N
U$1: SFH221; SFH_221
U$2: PINHD_SMD-3

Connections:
5V: C1.1, FB2.1, U$2.1
-5V: C2.1, FB1.1, U$2.2
GND_ANALOG: C1.2, C2.2, C5.2, C6.2, C7.2, C8.2, U1.3, U2.3, U$1.CATHODE, U$1.METAL_CASE, U$2.3
unnamed: C4.1, J2.2, R2.2, U2.1
unnamed: C4.2, R2.1, U2.4, U$1.ANODE_B
unnamed: C3.1, J2.1, R1.2, U1.1
unnamed: C3.2, R1.1, U1.4, U$1.ANODE_A
V+(5V): C6.1, C7.1, FB2.2, U1.5, U2.5
V-(-5V): C5.1, C8.1, FB1.2, U1.2, U2.2

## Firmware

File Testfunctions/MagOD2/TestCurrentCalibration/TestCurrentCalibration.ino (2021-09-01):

#include <SPI.h> // Communication
#include <Adafruit_GFX.h>    // Core graphics library
#include <Adafruit_ADS1015.h>  // ADC library

/* Help program that scans the PWM of the motordrivers and measures the current sensors adc4-6. If you connect a multimeter at the same time to the coils, you can make a graph of measured current versus real current */

/* TODO: There is a strange bug. Every time you change the channel, the adc outputs 19 or 20 for the first iteration. Only happens when the 12V is on and the coils are actuated.*/

#define RA8875_INT 16
#define RA8875_CS 5 
#define RA8875_RESET 17

/* MagOD2 has two ADS1115. 
   U2 with address pin to gnd, used for AIN0-3.
   U5 with address pin to VDD (3.3V), used for AIN4-7 */
#define ADS1015_ADDRESS_0 (0x48)// 1001 000 (ADDR -> GND)
#define ADS1015_ADDRESS_1 (0x49)// 1001 001 (ADDR -> VDD)
Adafruit_ADS1115 ads0(ADS1015_ADDRESS_0); //adc0-3;
Adafruit_ADS1115 ads1(ADS1015_ADDRESS_1); //adc4-7;

uint8_t Coil_x = 33; // pwm_x: output pin of the coils in the x direction
uint8_t Coil_y = 26; // pwm_y: output pin of the coils in the y direction
uint8_t Coil_z = 14; // pwm_z: output pin of the coils in the z direction
const uint32_t Frequency_PWM = 20000;    //set the pwm frequency of the coil-drivers
const int ledChannel_x = 3; /*0-15*/
const int ledChannel_y = 4; /*0-15*/
const int ledChannel_z = 5; /*0-15*/
const int resolution = 8; /* number bits resolution, 1-16 bit */
int Dir_x = 25;                /* direction pin of the coils in the x
				  direction low: output A of motor
				  driver is high and B is low
				  (positive direction), high: output A
				  of motor driver is low and B is high
				  (negative direction). See manual
				  MD13S page 6*/
int Dir_y = 27;                // direction pin of the coils in the y direction
int Dir_z = 12;                // direction pin of the coils in the z direction

/* help variable */

void setup () {
  Serial.begin(115200);

  /* Initialize the PWM */
 
 // Initialize channels 
  /*  channels 0-15, resolution 1-16 bits, freq limits depend on
       resolution ledcSetup(uint8_t channel, uint32_t freq, uint8_t
       resolution_bits);
     https://github.com/espressif/esp-idf/blob/master/docs/en/api-reference/peripherals/ledc.rst
  */

  ledcSetup(ledChannel_x, Frequency_PWM, resolution);
  ledcSetup(ledChannel_y, Frequency_PWM, resolution);
  ledcSetup(ledChannel_z, Frequency_PWM, resolution);

  ledcAttachPin(Coil_x, ledChannel_x);
  ledcAttachPin(Coil_y, ledChannel_y);
  ledcAttachPin(Coil_z, ledChannel_z);
    					
  /* Initialize the direction pins for the motor drives */
    /* sets the direction pin as output */
  pinMode(Dir_x, OUTPUT);
  pinMode(Dir_y, OUTPUT);
  pinMode(Dir_z, OUTPUT);
 

  /* Set the voltage */
  /* ledcWrite(channel, dutycycle)
     note that dutycycle ranges from 0-2^(resolution) set in ledcSetup
  2^11=2048*/
  ledcWrite(ledChannel_x, 0);
  ledcWrite(ledChannel_y, 0);
  ledcWrite(ledChannel_z, 0);

  /* Initialize ADC */
  ads0.setGain(GAIN_ONE);
  ads0.begin();
  ads1.setGain(GAIN_ONE);
  ads1.begin();
}

const int X=1;
const int Y=2;
const int Z=3;
int directions[]={Z}; //or {Y}, etc.
int num_dir=1;
// int directions[]={X,Y,Z}; 
// int num_dir=3;

void loop()
{
  int adc4, adc5, adc6, adc7; //Summed bit values of adc
  int ad4, ad5, ad6;//help variables for output adc

  int Dir_i = Dir_x;
  int Chan_i = ledChannel_x;

  Serial.println(directions[0]);
  
  for(int i = 0; i < num_dir; i = i + 1 )
    { 
      switch(directions[i]) {
      case X:
	Serial.println("X");
	Dir_i  = Dir_x;
	Chan_i = ledChannel_x;
	break;
      case Y:
	Serial.println("Y");
	Dir_i  = Dir_y;
	Chan_i = ledChannel_y;
	break;
      case Z:
	Serial.println("Z");
	Dir_i  = Dir_z;
	Chan_i = ledChannel_z;
	break;
      default:
	Serial.print("value not expected:");
	Serial.println(Dir_i);
      }
      
      for (double step = -1; step <= 1; step = step+0.2)
	{
	  /* Set the current direction */
	  if (step <  0) {digitalWrite(Dir_i, HIGH);};
	  if (step >= 0) {digitalWrite(Dir_i, LOW);};
	  /* Set the PWM, second value is relative to 2^resolution */
	  int PWM = fabs(step)*pow(2,resolution);//fabs is for doubles
	  ledcWrite(Chan_i, PWM);
	  delay(500);//wait for the system to settle

	  /* Read ADC1115 ports */
	  adc4 = 0;
	  adc5 = 0;
	  adc6 = 0;
	  int N = 150;
	  for (int j = 0; j < N; j++)
	    { ad4 = ads1.readADC_SingleEnded(0);
	      ad5 = ads1.readADC_SingleEnded(1);
	      ad6 = ads1.readADC_SingleEnded(2);
	      adc4 = adc4 + ad4;
	      adc5 = adc5 + ad5;
	      adc6 = adc6 + ad6;
	      // Serial.print(ad4);
	      // Serial.print(" ");
	      // Serial.print(ad5);
	      // Serial.print(" ");
	      // Serial.println(ad6);
	    }

	  if (step < 0)  {Serial.print("-");};
	  if (step >= 0) {Serial.print(" ");};
	  Serial.print(PWM);
	  Serial.print(", ");
	  Serial.print(adc4/N);
	  Serial.print(", ");
	  Serial.print(adc5/N);
	  Serial.print(", ");
	  Serial.println(adc6/N);
	}
      ledcWrite(Chan_i, 0); //Stop current
    }  
}

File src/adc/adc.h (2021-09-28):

/* adc.h
 MagOD libary 
 December 2020
 Photodiode readout
 Tijmen Hageman, Jordi Hendrix, Hans Keizer, Leon Abelmann 
*/
#ifndef adc_h
#define adc_h

//#include <Adafruit_ADS1015.h>  // ADC library, now included in standard libraries
#include "../MagOD_ADS1115/MagOD_ADS1115.h" // Modified Adafruit_ADS1015 lib


#include "../../MagOD.h"
#include "../led/led.h" // Needed for set_vrefs. adc and led are interdepenent. Perhaps solve in MagOD itself. TODO. LEON

/* addresses of ADS1115 ADC's */
#define ADS1115_ADDRESS_0 (0x48) // 1001 000 (ADDR -> GND)
#define ADS1115_ADDRESS_1 (0x49) // 1001 001 (ADDR -> VDD)
/* ESP32 pin that the ready pin of the ADC is attached to */
#define ADS1115_RDY 13                     
/* samplerate for adc0 */
#define sampleRateADC0 0 /* Sample rates: 0: 8 SPS, 1: 16 SPS, 2: 32
			    SPS, 3: 64 SPS, 4: 128 SPS, 5: 250 SPS, 6:
			    475 SPS 7: 860 SPS */

#if defined(_MAGOD1)
#define Temp_read //12 //Pin for NTC ADC
#endif
/* MagOD2 uses adc1 for reading temperature */


/* Definition of the buffer size, how many elements does it have */
#define bufferSize 1000
/* Buffer data structure type*/
typedef struct {
  uint8_t ch;                 // Channel that was measured on
  uint16_t val;               // Value that was measured
  unsigned long time;         // Time of the measurement
  /* the millis function returns a 32bit value meaning it will
     overflow after 49 days */
} bufferData_t;

/* readable names for the ADC channels */
#define SCAT  0 /* ads0 ADC0 Ain0 scattering photodiode */
#define DIODE 1 /* ads0 ADC1 Ain1 photodetector */
#define SPLIT 2 /* ads0 ADC2 Ain2 not connected */
#define LED   3 /* ads0 ADC3 Ain3 photodiode that measures LED directly */
#define IX    4 /* ads1 ADC0 A4 x-coils current monitor */
#define IZ    5 /* ads1 ADC1 A5 y-coils current monitor */
#define IY    6 /* ads1 ADC1 A6 z-coils current monitor */
#define NTC   7 /* ads1 ADC3 Ain7 ADCNTC temperature sensor */
// MagOD1 has DIODE_UP ad 2 DIODE_DOWN at 3.


class adc
{
 public:
  adc();
  void       initADC(); /* Start the ADCs with correct amplification,etc */
  bool       bufferEmpty();//Check if ADC0 buffer has data
  dataPoint  getDataPoint(); /* Get datapoint and convert*/

  /* void       set_vrefs(references &Vref, bool ref_all_wavelength, led myled);  */
  /* diodes     readDiodes(); // Read the signals from the photodiodes */
  /* double     readTemp(); //Read the temperature sensor */
  /* feedbacks  readFeedbacks();//Read the currents to the coils */
 private:
};

#endif

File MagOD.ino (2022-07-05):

/* MagOD version 2.5 */
/* Jan 2021 */
/* Tijmen Hageman, Jordi Hendrix, Hans Keizer, Leon Abelmann, Marcel
   Welleweerd, Dave van As, Ruthvik Bandaru, Rob Krawinkel */

/* Class definitions */
#include "MagOD.h"

/* Version of electronics is defined in MagOD.h */
#if defined(_KIST_1)
#warning "Compiling for KIST MagOD1.Change in MagOD.h"
#elif defined(_KIST)
#warning "Compiling for KIST MAGOD2. Change in MagOD.h"
#elif defined(_CEA)
#warning "Compiling for CEA MAGOD2. Change in MagOD.h"
#elif defined(_BAYREUTH)
#warning "Compiling for BAYREUTH MAGOD2. Change in MagOD.h"
#elif defined(_ASTON)
#warning "Compiling for ASTON MAGOD2. Change in MagOD.h"
#else
#error "No hardware version defined in MagOD.h"
#endif

#if (defined(_MAGOD1) && defined(ARDUINO_AVR_MEGA2560)) || \
    (defined(_MAGOD2) && defined(ARDUINO_ESP32_DEV))


/* ############## Global variables ########### */

/* Update frequencies */
#if defined(_MAGOD1)
float freq_meas = 7; //Measurement frequency in Hz
// For Arduio in MagOD1: tested up to 7 Hz. Can be 20 Hz without saving data. Can be 30 Hz if we optimize doMeasurement. Can be 100 Hz if we only read one adc. Can be 700 Hz theoretically...
#elif defined(_MAGOD2)
// MagOD2 measures on interupt basis on ADC0. Set ADC clock in adc.h
float freq_meas = 1; /* Measurement frequency for ADC1 (currents,
			temperature) in Hz */
#endif
float freq_screen = 4; //Screen update frequency in Hz


/* Program menu settings */
recipe recipes_array[MaxRecipes]; // Array of recipes
int    program_cnt = 0; /* Current recipe selected, default 0 */
int    program_nmb = 0; /* Total number of recipes in recipes_array
			  [0..program_nmb] */

/* ADCO works on interupt. Data is stored in buffer. See adc.cpp */
// Handle to refer to the task that does the ADC measurement
TaskHandle_t readADC0Handle; 
// Handle for the buffer
QueueHandle_t dataQueueHandle;

/* ADC settings */
#if defined(_MAGOD1)
double adsMaxV0;  //max voltage that can be measured by the ADC
#elif defined(_MAGOD2)
double adsMaxV0,adsMaxV1;  //max voltages, for two ADCs
#endif

/* State variables (global) used in this program */
bool doMeasurementFlag = false; //Read the ADC inputs. Only ADC1 for MagOD2
bool screenUpdateFlag  = false; //Update the screen
bool Updatecurrentflag = false; //Do a current calibration
bool Exit_program_1    = HIGH;  //The program should end

/* Status parameters */
bool isRecording       = false; //We are measuring
bool SDpresent         = false; //There is a readable SD card in the slot
uint8_t prevButton     = 0;     //Status of the button
bool autoCmag          = false; //Recipe in in automatic Cmag format

/* Extra control parameters, kind of obsolete */
bool sendToSerial      = 0;     /*Do we send files during the
				   measurement over serial port? */
bool save_extra_parameter = 0;  /*set this to 1 when you want to store
				  an extra parameter in the header of
				  the .CVS file (this can be any
				  parameter which makes it easier for
				  dataprocessing, for instance which
				  fields are used) */
double extra_par = 0.0;         /*value of this extra parameter
				   (specifiy this in the
				   initialization function) */

/* Init classes */
adc myadc;
screen myscreen;
timer mytimer;
led myled;
buttons mybuttons;
field myfield;
fileandserial myfile;
recipes myrecipes;
IO *  myIO; /* Wraps IO for recipes, used by TestRecipes. Perhaps
	       merge with fileandserial. LEON */
File dataFile; /* file handle for output file */


/* FTP server */
/* To connect to your wifi network, we expect file a 'password.h' in
local directory with contents: 
const char* ssid = "MyWifiNetwork"; //WiFi SSID 
const char* password = "PasswordForThatNetwork"; //WiFi Password
*/
#include "password.h" //expected in local directory
/* hostname that may appear on your network */
const char* host = "magod"; //HERE? LEON
/* FTP server */
FtpServer ftpSrv;
bool serverStarted = false;

/* Should this be here? LEON*/
#if defined(_MAGOD2)
hw_timer_t * timer1 = NULL;
hw_timer_t * timer3 = NULL;
hw_timer_t * timer4 = NULL;
#endif

/* The measured parameters */
dataPoint nextData = {0,0,0};   /* Next datapoint from buffer */
diodes Vdiodes = {0,0,0};       /* Photodetector signals [V] */
double Temperature = 0;         /*Temperature estimated from
				  temperature sensor*/
references Vrefs = {1,1,1,1,PDOFFSET}; /* Reference values of photodector
				  signals. Current value and three
				  different colors. Initialize to 1 to
				  get meaningful OD */
feedbacks Currents = {0,0,0};   /* Current feedback values */

/* Parameters for displayed graph */
dataPlot graph[GRAPH_LENGTH] = {0,0};/* Graph with datapoints and
					their color to display */
int graphCount      = 0; // Index counting datapoints in graph
int graphLength     = GRAPH_LENGTH; // Total lengt. <= GRAPH_LENGTH
long startTime      = millis(); /* Time at which the measurement
				   started */
long lengthTimeAxis = 200000; /* x-axis ranges from 0..lengthTimeAxis (ms)*/

/* Calculated parameters */
double OD = 0;                 /*Optical Density. Calculated in
				 CaldOD() */
cmagStruc Cmag = {0};  /* Cmag calculation parameters */

/* Time parameters */
unsigned long time_of_start = millis(); /*Time at which the
					measurement was started.*/
unsigned long time_last_field_change = millis(); /*Time since the last
					    field step */

/* LED parameters */
//int LED_type = GREEN; //The color of the LED
int LEDs[3] = {RED, GREEN, BLUE};
#if defined(_MAGOD2)
int LED_intensity[3] = {15,65,95};//Values that don't saturate the photodiode
#endif
// OBSOLETE? LEON
bool ref_all_wavelength = 0; //Only MagOD1. Set this to 1 for specific programs where you work with multiple wavelengths in a single measurement (such that it stores the reference value of all 3 wavelengths. Can be removed, but you need to rewrite set_vrefs

/* Declare variables to define the field sequence */
int B_nr_set = 1; //the length of the field sequence array [0..B_nr_set];
int Looppar_1 = 0; //Track at which point of the field-array we are

int Nr_cycles = 0; //The number of cycles throught the array, a value of 0 means an infinite amound of cycles
int Looppar_2 = 0; //Track how many times we cycled through the recipe

/* Note, the definitions don't seem to work. Only the first element in the array is set to that value. Instead, I initialize the arrays in recipes.cpp */
double B_arrayfield_x[B_NR_MAX] = {0.0}; //an array containing B_Nr_set elements for the field in the x-direction, each element has to be an integer between -256 and 256 and negative numbers can be used for opposite directions
double B_arrayfield_y[B_NR_MAX] = {0.0}; //Same for y
double B_arrayfield_z[B_NR_MAX] = {0.0}; //Same for z
unsigned long Switching_time[B_NR_MAX] ={1000};
int LEDColor_array[B_NR_MAX] = {GREEN}; // Default color is green
int LEDInt_array[B_NR_MAX] = {0}; // Default intensity is off

bool Gradient_x[B_NR_MAX]={1};  //determines whether both coils must be on or just one of them for the x-direction, 0 is both on, 1 is only one. When the set of coils is connected, set to 1. Note that MagOD2 no longer has relays to do this automatically, you need to manually route the currents through one coil only.
bool Gradient_y[B_NR_MAX] = {1};  //same for y
bool Gradient_z[B_NR_MAX] = {1};  //same for z
int i=0;

/*** Top level functions ***/

/** Timer triggers **/
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

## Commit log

2019-01-13 Version that compiles and runs on Arduino Mega 2560 with 1.8" screen. Not tested on real MagOD
2019-04-07 deleted arduino dir
2019-04-07 removed TestTFT50 directory ,contains material that should not be publishe
2019-05-09 MagOD1 compiling and running Added Matlab code for analysis of datafiles
    [f119.csv, f119_1.csv, f119_10.csv, f119_100.csv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]
2019-09-18 made testarea for new recipes function
    [RECIPES.CSV]
2019-09-21 changed file format
    [RECIPES.CSV]
2019-09-26 made new examples
    [f119.csv, f119_1.csv, f119_10.csv, f119_100.csv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]
2020-02-15 Adjustable LED intensity during program. Test function for LED Test function for TFT screen
2020-03-18 Introduced ReadRecipes: read RECIPES.CSV from Flash card. First only test to check if recipe is read well.
    [RECIPES.CSV]
2020-03-21 Try to test recipes reading on computer, rather than ESP32
2020-04-03 TestRecipes, split of the command line and Arduino versions in an organised way
    [RECIPES.CSV]
2020-04-03 new recipes.csv
    [RECIPES.CSV]
2020-05-27 Select samplerate ADC Recipes are read from csv file, recipes.* compatible with command line version
2020-05-27 Adapted MagOD.* for new recipes routines New testing routines
    [RECIPES.CSV]
2020-05-31 Tweaks on screen layout. Added example RECIPES.CSV
    [RECIPES.CSV]
2020-06-07 Corrected error in field calibration. Tweaked screen layout.
    [RECIPES.CSV]
2020-07-10 Nasty bug in z-field, lost attachment to channel
    [RECIPES.CSV]
2020-10-15 Modifications preparing for the Bayreuth system. Introduced calibration.h for all system dependent settings. Fixed error with Vref setting. Also switched on the led immediately after loading recipe.
    [RECIPES.CSV]
2021-02-14 fixed error for number of recipes sequences > 15. Experiments with python reading of data files
    [RECIPES.CSV, f0001.csv, f0002.csv, f0003.csv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]
2021-09-01 fixed error in calculation OD on screen
    [RECIPES.CSV, dataX.csv, dataY.csv, dataZ.csv]
2021-09-28 Implement autoCmag recipe, which calculates OD and Cmag automatically and displays on the touchscreen
    [RECIPES.CSV]
2021-10-24 Added screen reset. Code cleanup.
    [RECIPES.CSV]
2022-07-05 Copied from Dropbox
    [HDMIWiring.xls, ODMeter-2018-11-06-17-38-10.sch, ODMeter-B.Cu.gbl, ODMeter-B.Mask.gbs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]
2022-07-05 correct incorrect directory structure
    [6pin.ipt, Assembly.iam, CuvetteHolders.scad, CuvetteHolders.stl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]
